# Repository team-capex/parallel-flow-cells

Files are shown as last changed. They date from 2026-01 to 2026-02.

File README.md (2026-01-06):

# User Guide for Parallel MEA / H-Cell Setups

## Install Dependencies from PyProject

Build venv in root directory:

```
python -m venv .venv
```

Upgrade pip:

```
.venv/bin/pip install --upgrade pip
```

Install dependencies into new venv:

```
.venv/bin/pip install -e .
```

Activate venv:

```
source .venv/bin/activate
```

Note: Replace *bin* with *Scripts* if using windows.

## Calibrating Load Cells

## Other Requirements

- Platformio vscode extension to flash firmware to PCBs
- RS485 converter for MFC

## Hardware References

See [BOM](part_files/BOM.pdf) for complete list.

1. [1kg load cells](https://www.digikey.dk/da/products/detail/adafruit-industries-llc/4540/12323569?srsltid=AfmBOop3O_A9xKGq612NTgOTVNnTNE8ITZH4t8R0--68j-zy2UcEIYY0)
2. [0.5slm MFC](https://sensirion.com/products/catalog/SFC5500-05slm)
3. [5slm MFC](https://sensirion.com/products/catalog/SFC6000D-5slm)
4. [3/2 Solenoid Valves](https://www.festo.com/dk/en/a/196132/)
5. [9QX Peristaltic Pump](https://www.boxerpumps.com/peristaltic-pumps-for-liquid/9qx/)

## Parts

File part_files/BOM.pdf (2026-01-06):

Part Number Description Material Cost (DKK) Qty Total DKK Supplier Link MEA x6
| Custom cells | Titanium Grade 2 | | | 4,800.00 kr. WeNext
5004A11 | Toggle clamp | Steel | 118.00 kr. | 6 | 708.00 kr. Goodhand | https://goodhanduk.co.uk/vertical-toggle-clamps/vertical-toggle-clamp-overall-height-60mm-overall-length-94mm-holding-force-150dan-adjustable-flat-101-200kg-51-100mm-51-100mm-21-30mm-51-75mm-m8-gh-13007
| OR 18,77 X 1,78 | Viton/EPDM | 6.30 kr. | 6 | 37.80 kr. MW | https://ehandel.mw.dk/da/178-viton/o-ring-1877x178-viton-
| Barbed to Male 1/4"-28, ID 1/16" | ETFE | 430.00 kr. | 2 | 860.00 kr. Darwin | https://darwin-microfluidics.com/products/barbed-to-male-1-4-28-adapter-for-1-16-or-1-8-id-flexible-tubing-pack-of-10
| Platinum-cured Silicone Tubing (15 m) 2mm ID | Silicone | 178.00 kr. | 1 | 178.00 kr. Darwin
HPS-6-3.1-18-N | Plastic spacer (m3 x 6mm dia) | Nylon | 2.00 kr. | 36 | Accu | https://www.accu.co.uk/cylindrical-spacers/463974-HPS-6-3-1-18-N
SSCF-M4-35-A2 | M4x35mm | A2 | | 24 | Accu
SSCF-M3-25-A2 | M3x25mm | A2 | | 36 | Accu
SSCF-M3-10-A2 | M3x10mm | A2 | | 24 | 600.00 kr. Accu

CO2
1649-SFC6000D-5SLM-ND | MFC for CO2 (I2C, 24V, 210mA) | | 2,174.00 kr. | 1 | 2,174.00 kr. Digikey | https://www.digikey.dk/da/products/detail/sensirion-ag/sfc6000d-5slm/17829202
1528-4545-ND | 6mm PVC tubing | PVC | 12.00 kr. | 1 | 12.00 kr. Digikey | https://www.digikey.dk/da/products/detail/adafruit-industries-llc/4545/11627733?gclsrc=aw.ds&gad_source=1&gad_campaignid=19553954322&gbraid=0AAAAADrbLljpWXnvO9wyNsjCb2PZ5PgfI&gclid=Cj0KCQjw58PGBhCkARIsADbDilx9DRJTLxXdIQNYD9Ui8bdA7DL3JmfsgUJsoTZtAmLSkMoV-oUUZvMaAtvrEALw_wcB
4829-MA08FAHD04RA-20CB25-ND | M8 4p cable | | 57.00 kr. | 1 | 57.00 kr. Digikey | https://www.digikey.dk/da/products/detail/finecables/MA08FAHD04RA-20CB25/18077552?gclsrc=aw.ds&gad_source=1&gad_campaignid=19561463036&gbraid=0AAAAADrbLlhww0wDtSavdPzRh915kKBFp&gclid=Cj0KCQjw58PGBhCkARIsADbDilz7R3Wi_kISS25-sVtoRoq_2h4j312e7uNhwl514B2i2WKu11Ijz_waApS6EALw_wcB
WM17189-ND | Molex Micro-Lock Plus 0451110606 | | 19.00 kr. | 1 | 19.00 kr. Digikey | https://www.digikey.dk/da/products/detail/molex/0451110606/7915903?s=N4IgTCBcDaILIHsA2BTAHgAjgSwMYCcEBaAGQVwGsMAFJAVwGcMAGAFgFYBGb5gNj5ABdAL5A
FR-4-1/4 | Distributor Block, 3 Outlet, G1/4, FR Series | Al | 140.00 kr. | 3 | 420.00 kr. RS | https://dk.rs-online.com/web/p/manifold-baser-undersegmenter-og-endesegmenter/2890837?cm_mmc=DK-PLA-DS3A-_-google-_-CSS_DK_DK_PMax_Low-Price-Low-Performance-_--_-2890837&matchtype=&&gclsrc=aw.ds&gad_source=1&gad_campaignid=22922140264&gbraid=0AAAAADkeWNPjzJvbKHpMcgwmJvPYL_CWR&gclid=Cj0KCQjwrc7GBhCfARIsAHGcW5Vg9IRaZ06QjpGmncXCGT5fjW5V8vwqqtyP1wgSseHVZzooB2Mm_mAaAqvkEALw_wcB
QS-G1/4-6 | Pneumatic Fitting, Push-In Fitting, G1/4, 14 bar, 6 mm, Brass, QS (10) | Brass | 196.00 kr. | 1 | 196.00 kr. RS | https://dk.farnell.com/festo/qs-g1-4-6/push-in-fitting-6mm-g1-4/dp/3432186
B-1/4 | Pneumatic Fitting, Push-In Fitting, G1/4, 18 mm, Steel, (10) | Steel | 114.00 kr. | 1 | 114.00 kr. RS | https://dk.farnell.com/festo/b-1-4/push-in-fitting-18mm-g1-4/dp/3436726
QSF-1/4-4-B | Pneumatic Fitting, Push-In Fitting, G1/4, 14 bar, 4 mm, Brass, QSF | Brass | 33.00 kr. | 6 | 198.00 kr. Farnell | https://dk.farnell.com/festo/qsf-1-4-4-b/push-in-fitting-4mm-g1-4-9-7mm/dp/3432275?gross_price=true&CMP=KNC-GDK-GEN-Shopping-Pmax-High-ROAS-Test-1333&mckv=_dc|pcrid||&gad_source=1&gad_campaignid=20746710150&gbraid=0AAAAAD8yeHkMi_H50LZUAWp5PPbQ_94pU&gclid=CjwKCAjw89jGBhB0EiwA2o1Onx2IczdmaHkpGrZ8EoYNKaaRZJsceP5hbWil1OpdHAXtCcThY-iGPhoCY5EQAvD_BwE
NPFC-D-2G14-M | Festo NPFC Lige fitting G 1/4, G 1/4 han til G 1/4, Med gevind | Brass | 68.00 kr. | 1 | 68.00 kr. RS | https://dk.rs-online.com/web/p/pneumatik-fittings/2502692?cm_mmc=DK-PLA-DS3A-_-google-_-CSS_DK_DK_PMax_Low-Price-Low-Performance-_--_-2502692&matchtype=&&gclsrc=aw.ds&gad_source=1&gad_campaignid=22922140264&gbraid=0AAAAADkeWNMbt_YSda_Ss2Pe8KWR1JZ7d&gclid=CjwKCAjw89jGBhB0EiwA2o1On4_b-wo6nXAr70IkGOkNC9hPqeI6ZpGywWgbqwnNWUBGY88c-LlPtBoCWeoQAvD_BwE
QSM-M3-4-I | Pneumatic Fitting, Push-In Fitting, M3, 14 bar, 4 mm, Steel, QSM | Steel | 30.00 kr. | 12 | 360.00 kr. Farnell | https://dk.farnell.com/festo/153314/push-in-fitting-4mm-m3-8mm/dp/3432137?gross_price=true&CMP=KNC-GDK-GEN-Shopping-Pmax-High-ROAS-Test-1333&mckv=_dc|pcrid||&gad_source=1&gad_campaignid=20746710150&gbraid=0AAAAAD8yeHkMi_H50LZUAWp5PPbQ_94pU&gclid=CjwKCAjw89jGBhB0EiwA2o1On-xq_k4-8pehjHkxhBXVDBrv5aZdelxS_hp0dAAXmB-WaFDIt3CJrRoCQbAQAvD_BwE
QSMT-4 | Pneumatic Fitting, Push-In T-Fitting, 14 bar, 4 mm, PBT (Polybutylene Terephthalate), QST | PBT | 33.00 kr. | 5 | 165.00 kr. Farnell | https://dk.farnell.com/festo/153128/push-in-t-fitting-4mm-10mm/dp/3432081?gross_price=true&CMP=KNC-GDK-GEN-Shopping-Pmax-High-ROAS-Test-1333&mckv=_dc|pcrid||&gad_source=1&gad_campaignid=20746710150&gbraid=0AAAAAD8yeHkMi_H50LZUAWp5PPbQ_94pU&gclid=CjwKCAjw89jGBhB0EiwA2o1On9Ke7jQRASimdTHQLkaKA-uQwV2e4eMabnsTtx5DLgJlGQeRKKp_ehoCmqwQAvD_BwE
PEN-4X0,75-BL | Pneumatic Tubing, 4 mm, 2.7 mm, PE (Polyethylene), Blue, 10 bar, 50 m | PE | 164.00 kr. | 1 | 164.00 kr. Farnell | https://dk.farnell.com/festo/pen-4x0-75-bl/plastic-tubing-10bar-pe-50m-blue/dp/3432523?gross_price=true&CMP=KNC-GDK-GEN-Shopping-Pmax-High-ROAS-Test-1333&mckv=_dc|pcrid||&gad_source=1&gad_campaignid=20746710150&gbraid=0AAAAAD8yeHkMi_H50LZUAWp5PPbQ_94pU&gclid=CjwKCAjw89jGBhB0EiwA2o1OnzBm_ssv7OcDU8E3JuuKJTVj9dxXW-fRRRptIhBTt02IWX2fsSySehoCNBcQAvD_BwE
304-005 | RS PRO 24V dc AC/DC-adapter, Ekstern strømforsyning, 1A, 24W, Europæisk stik | | 134.00 kr. | 1 | 134.00 kr. RS | https://dk.rs-online.com/web/p/ac-dc-adaptere/0304005?srsltid=AfmBOoqRQSO9QZzJjiM4ApOePkaanLnN2yxJvQekZTMz0jzVhUAgkOK8KCM
MHE2-M1H-3/2O-M7 | Air Solenoid Valve, 3/2 Way, Closed, QS-4, -0.9 bar to 8 bar, 100 l/min | | 300.00 kr. | 6 | 1,800.00 kr. Rowse | https://www.rowse-pneumatics.co.uk/festo-mhe2-m1h-3-2g-qs-4
QSM-M7-4-I | Male thread M7 to 4mm tubing | | 222.00 kr. | 1 | 222.00 kr. WATTOO | https://www.wattoo.dk/festo-lige-forskruning-indstik-qsm-m7-4-i-10-stk-3980020634#ws-productView-desc
1649-SFC5500-0.5SLM-ND | MFC for CO2 (I2C, 24V, 210mA) | | 9,600.00 kr. | 1 | Digikey | https://www.digikey.dk/da/products/detail/sensirion-ag/sfc6000d-5slm/17829202
QSM-M3-4-I | Pneumatic Fitting, Push-In Fitting, M3, 14 bar, 4 mm, Steel, QSM | Steel | 30.00 kr. | 4 | 120.00 kr. Farnell | https://dk.farnell.com/festo/153314/push-in-fitting-4mm-m3-8mm/dp/3432137?gross_price=true&CMP=KNC-GDK-GEN-Shopping-Pmax-High-ROAS-Test-1333&mckv=_dc|pcrid||&gad_source=1&gad_campaignid=20746710150&gbraid=0AAAAAD8yeHkMi_H50LZUAWp5PPbQ_94pU&gclid=CjwKCAjw89jGBhB0EiwA2o1On-xq_k4-8pehjHkxhBXVDBrv5aZdelxS_hp0dAAXmB-WaFDIt3CJrRoCQbAQAvD_BwE
QSM-M5-4-I | Pneumatic Fitting, Push-In Fitting, M5, 14 bar, 4 mm, Steel, QSM | Steel | 30.00 kr. | 4 | 120.00 kr. RS | https://dk.rs-online.com/web/p/pneumatik-fittings/1216038

Liquids
| 9800.73 9QX stepper 3 roller (ID Ø 3.5 mm - single) | | 962.00 kr. | 2 | 1,924.00 kr. Boxer
| 9000.324 9QX 3.5mm ID tubing | Innovasil | 90.00 kr. | 2 | 180.00 kr. Boxer
| T-fittings for liquid manifold: 3.2mm ID (5 per manifold) | PP | 380.00 kr. | 1 | 380.00 kr. Darwin | https://darwin-microfluidics.com/products/masterflex-t-barb-connectors-pack-of-10
| Platinum-cured Silicone Tubing (15 m) 2 or 3mm ID | Silicone | 178.00 kr. | 1 | 178.00 kr. Darwin
102-PH-008-4MM | 100 Series Micro Peristaltic Pump (0.8mm Viton tubing) | | 140.00 kr. | 4 | 560.00 kr. Williamson | https://www.wmcpumps.com/SKU1-134
8HS15-0304S | Nema 11 Bipolar 1.8deg 4Ncm(5.7oz.in) 0.6A 20x20x39.3mm 4 Wires | | 120.00 kr. | 4 | 480.00 kr. StepperOnline | https://www.omc-stepperonline.com/nema-8-bipolar-1-8deg-3ncm-4-25oz-in-0-3a-12v-20x20x38mm-4-wires-8hs15-0304s
| Mini Peristaltic Pump | | 100.00 kr. | 8 | 800.00 kr. Frugo | https://www.fruugo.dk/mini-peristaltic-pump-high-quality-for-laboratory-bioengineering-g528-dc12vtype-c/p-314459620-701052377?language=en&ac=google&utm_source=google&utm_medium=paid&asc=pmax&gad_source=1&gad_campaignid=20975253578&gbraid=0AAAAADpXug2rU-1W62fdGEQqKVeoOzLIN&gclid=Cj0KCQiAgvPKBhCxARIsAOlK_Erhti6nMGFpah9tsT6SidzKpgmbqzjA4kZy3KL463TXhfh0PgX31E4aAvdfEALw_wcB
EGS11-G10 | EG Series Planetary Gearbox Gear Ratio 10:1 | | 200.00 kr. | 4 | 800.00 kr. StepperOnline | https://www.omc-stepperonline.com/eg-series-planetary-gearbox-gear-ratio-10-1-backlash-15-arc-min-for-nema-11-stepper-motor-egs11-g10
ID-P-642 | Female Luer to Male 10-32 Coned Adapters (pack of 5) | PP | 253.00 kr. | 1 | 253.00 kr. Darwin | https://darwin-microfluidics.com/products/female-luer-to-male-10-32-coned-adapters-pack-of-5
| Male Luer Lock to Barb Adapters | PP | 160.00 kr. | 1 | 160.00 kr. Darwin

HCELL x2
| Custom cells | PEEK/SS | | | 7,750.00 kr. WeNext
| Membrane O-Ring (18x1.5) | Viton | | 1 | 300.00 kr. MWilhelmsen | https://ehandel.mw.dk/da/150---152-viton/o-ring-18x15-viton-

Reference Electrode O-Ring (1.42x1.52) | Viton | 1 | MWilhelmsen | https://ehandel.mw.dk/da/150---152-viton/o-ring-142x152-viton-
PEEK Needle O-Rings (1.42x1.52) | Viton | 1 | MWilhelmsen
Lid O-Ring (12.42x1.78) | Viton | 1 | MWilhelmsen | https://ehandel.mw.dk/da/178-viton/o-ring-1242x178-viton-
Button O-Ring (6.75x1.78) | Viton | 1 | MWilhelmsen | https://ehandel.mw.dk/da/178-viton/o-ring-675x178-viton-
Face Seal O-Ring (15.62x1.78) | Viton | 2 | MWilhelmsen | https://ehandel.mw.dk/da/178-viton/o-ring-156x178-viton-
Sample Holder O-Ring (1.5x13) | FKM | 1 | RS | https://dk.rs-online.com/web/p/pakninger-og-o-ringe/1965679
4mm check valve | | 2 | RS | https://dk.rs-online.com/web/p/pneumatik-kontraventiler/9160934?cm_mmc=DK-PLA-DS3A-_-google-_-CSS_DK_DK_PMax_Low-Price-High-Performance-_--_-9160934&matchtype=&&gclsrc=aw.ds&gad_source=1&gad_campaignid=21368103075&gbraid=0AAAAADkeWNOhqKHZ-wnmj1lLo4dak1vKV&gclid=Cj0KCQjw9obIBhCAARIsAGHm1mTXmxO7bYi1EcSHGXpSH-vTNFiibPHKBHfGIG0wtLczniOT5oRMeXMaArEPEALw_wcB

Other
1528-4540-ND | 1kg Load Cell
| | 4 | 350.00 kr. Digikey | https://www.digikey.dk/da/products/detail/adafruit-industries-llc/4540/12323569?srsltid=AfmBOorwMf2knGiM3Ey5qxezQkc4qGCeHyW89jkVCpoIuLHWATXuRHIX

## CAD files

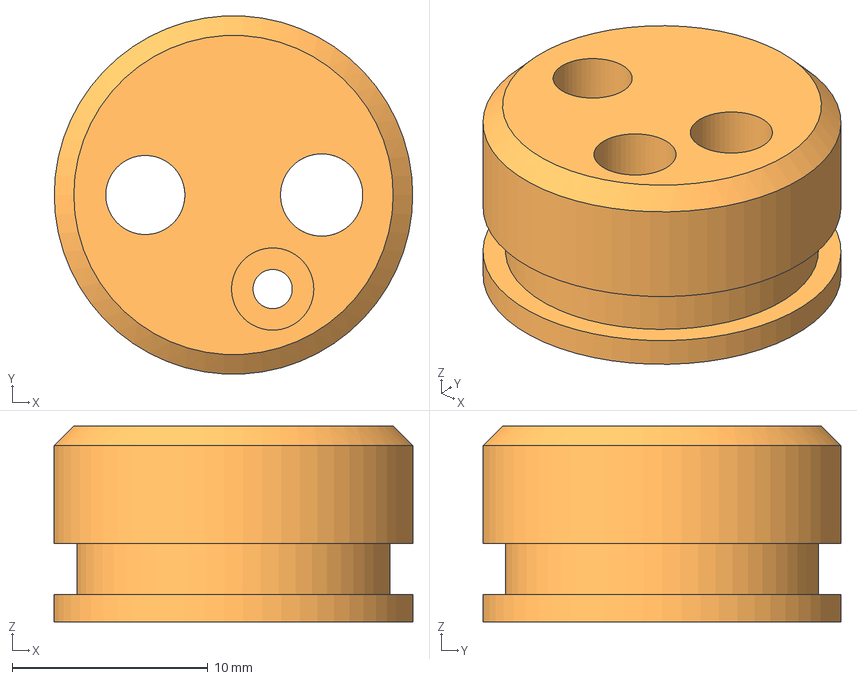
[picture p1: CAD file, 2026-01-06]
part_files/H-Cell - Counter Lid.step
18.3 x 18.3 x 10.0 mm

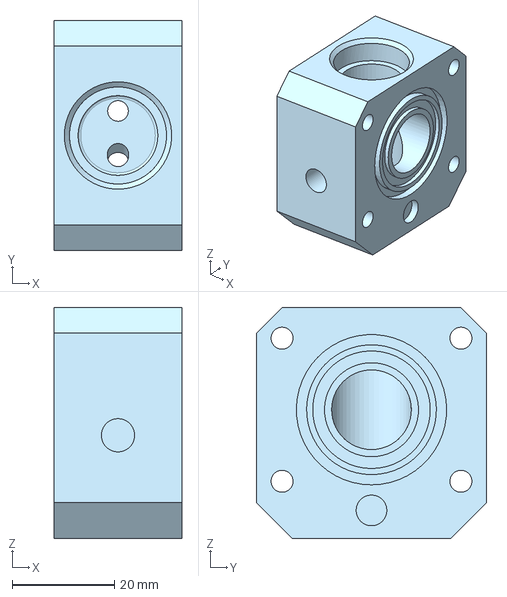
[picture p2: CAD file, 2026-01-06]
part_files/H-Cell - Counter Cell.step
25.0 x 45.0 x 45.2 mm

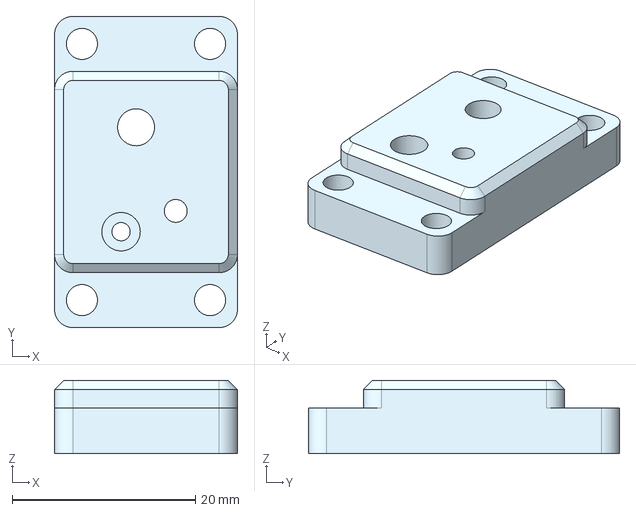
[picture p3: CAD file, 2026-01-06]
part_files/H-Cell - Working Lid.step
20.0 x 34.0 x 8.00 mm

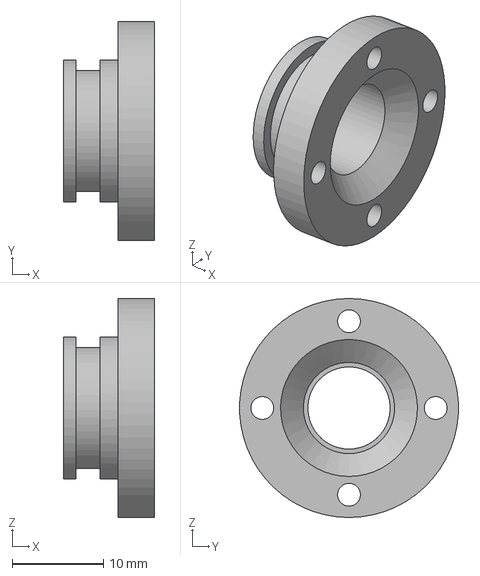
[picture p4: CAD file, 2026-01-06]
part_files/H-Cell - Sample Holder.step
10.0 x 24.0 x 24.0 mm

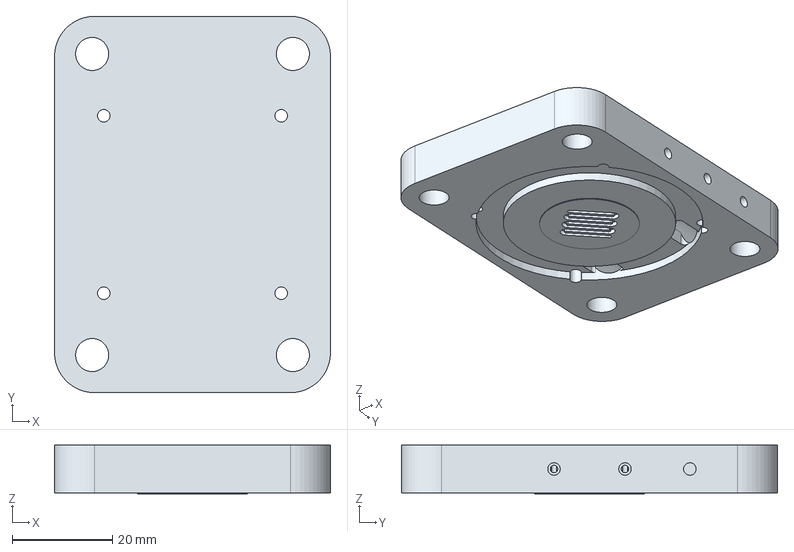
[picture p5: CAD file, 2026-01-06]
part_files/CATHODE_PLATE_TI - REV1.step
55.0 x 75.0 x 9.73 mm

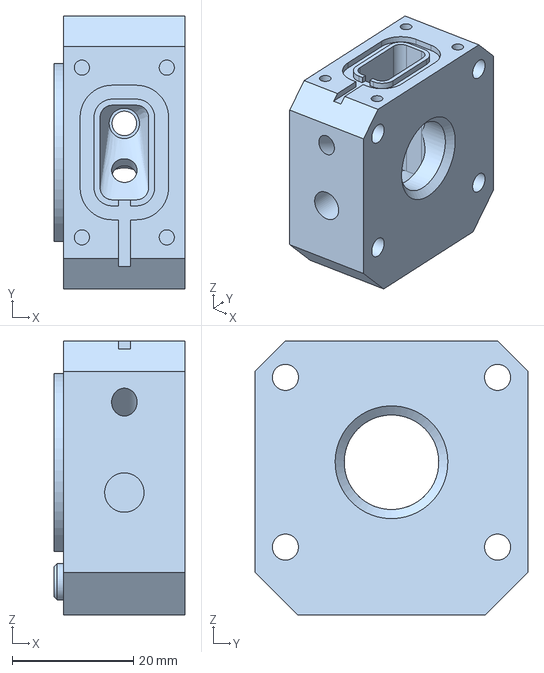
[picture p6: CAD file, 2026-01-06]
part_files/H-Cell - Working Cell.step
21.6 x 45.0 x 45.2 mm

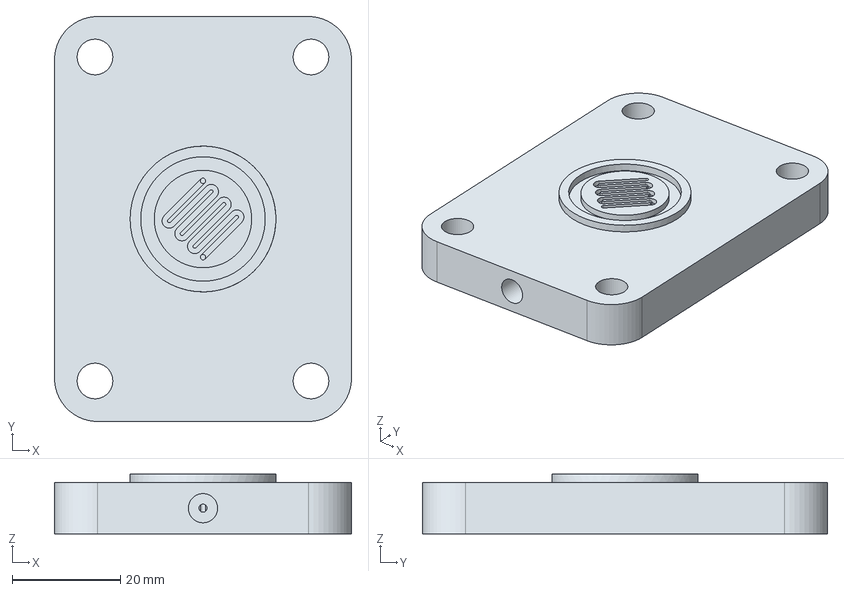
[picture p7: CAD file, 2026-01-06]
part_files/ANODE_PLATE_TI - REV1.step
55.0 x 75.0 x 11.1 mm

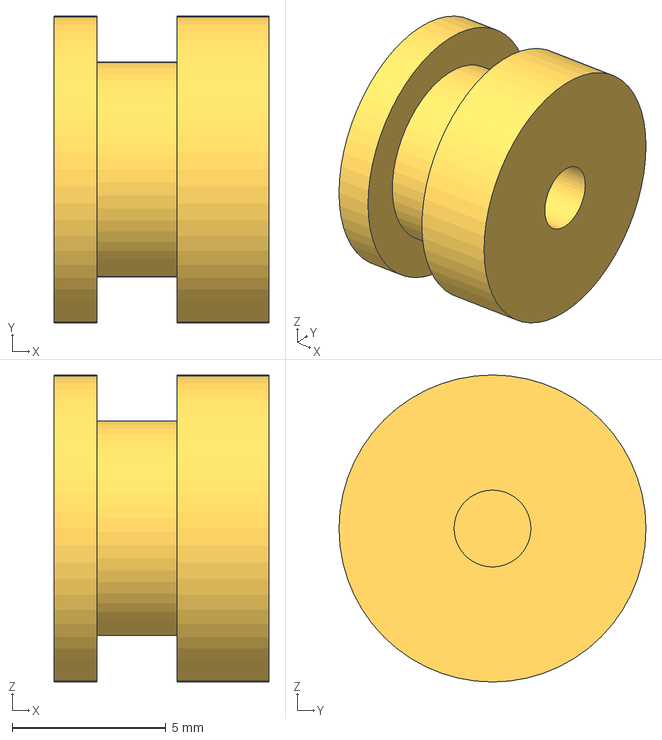
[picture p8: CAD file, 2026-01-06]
part_files/H-Cell - Sample Press.step
7.00 x 10.0 x 10.0 mm

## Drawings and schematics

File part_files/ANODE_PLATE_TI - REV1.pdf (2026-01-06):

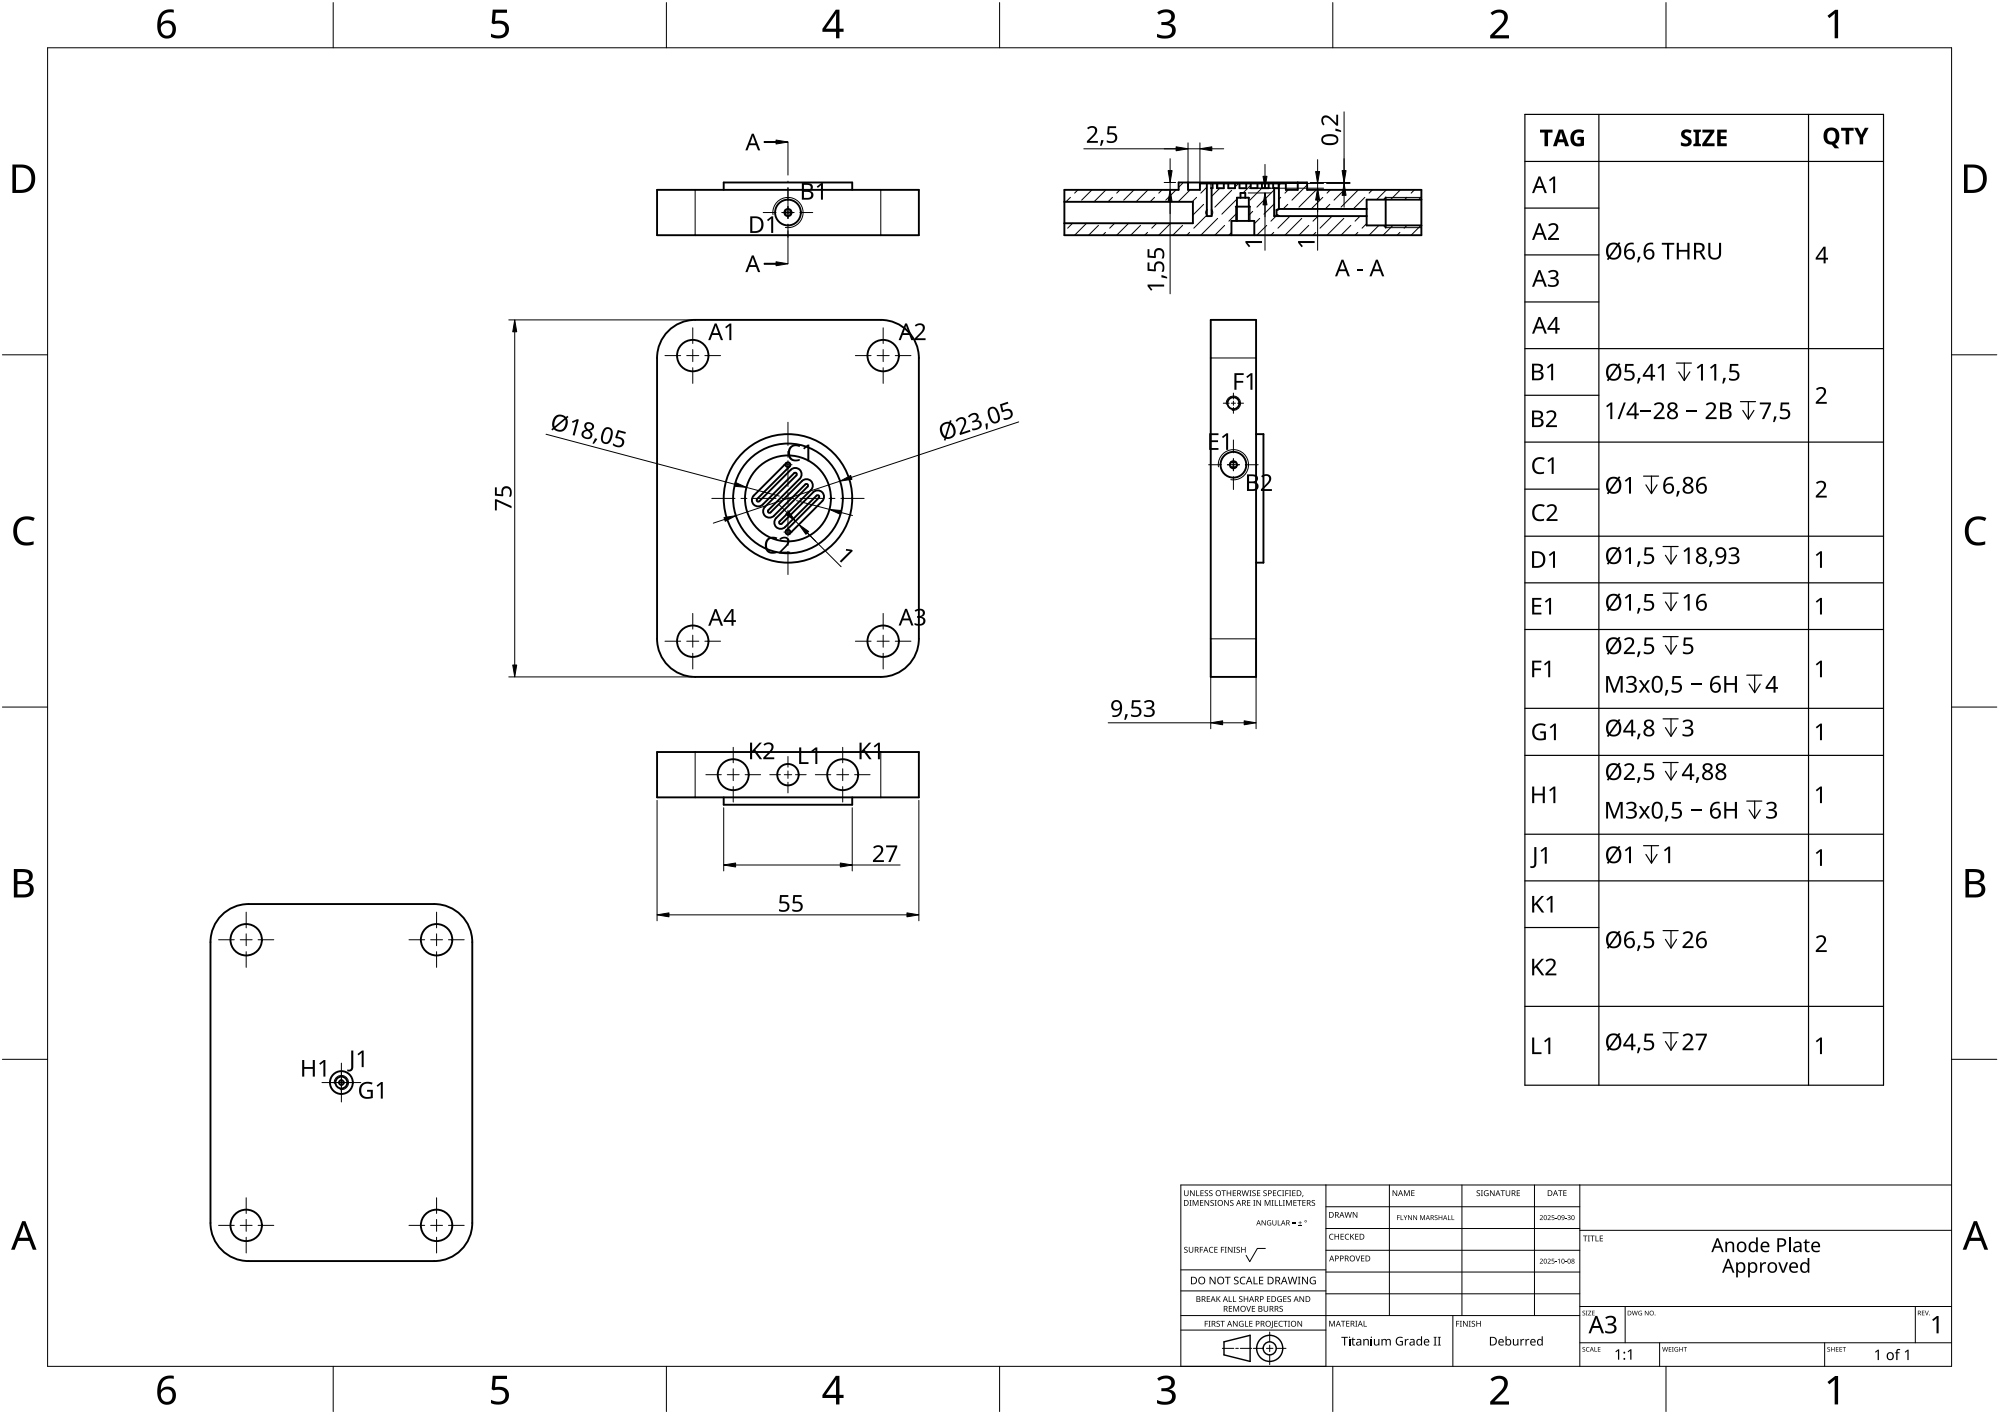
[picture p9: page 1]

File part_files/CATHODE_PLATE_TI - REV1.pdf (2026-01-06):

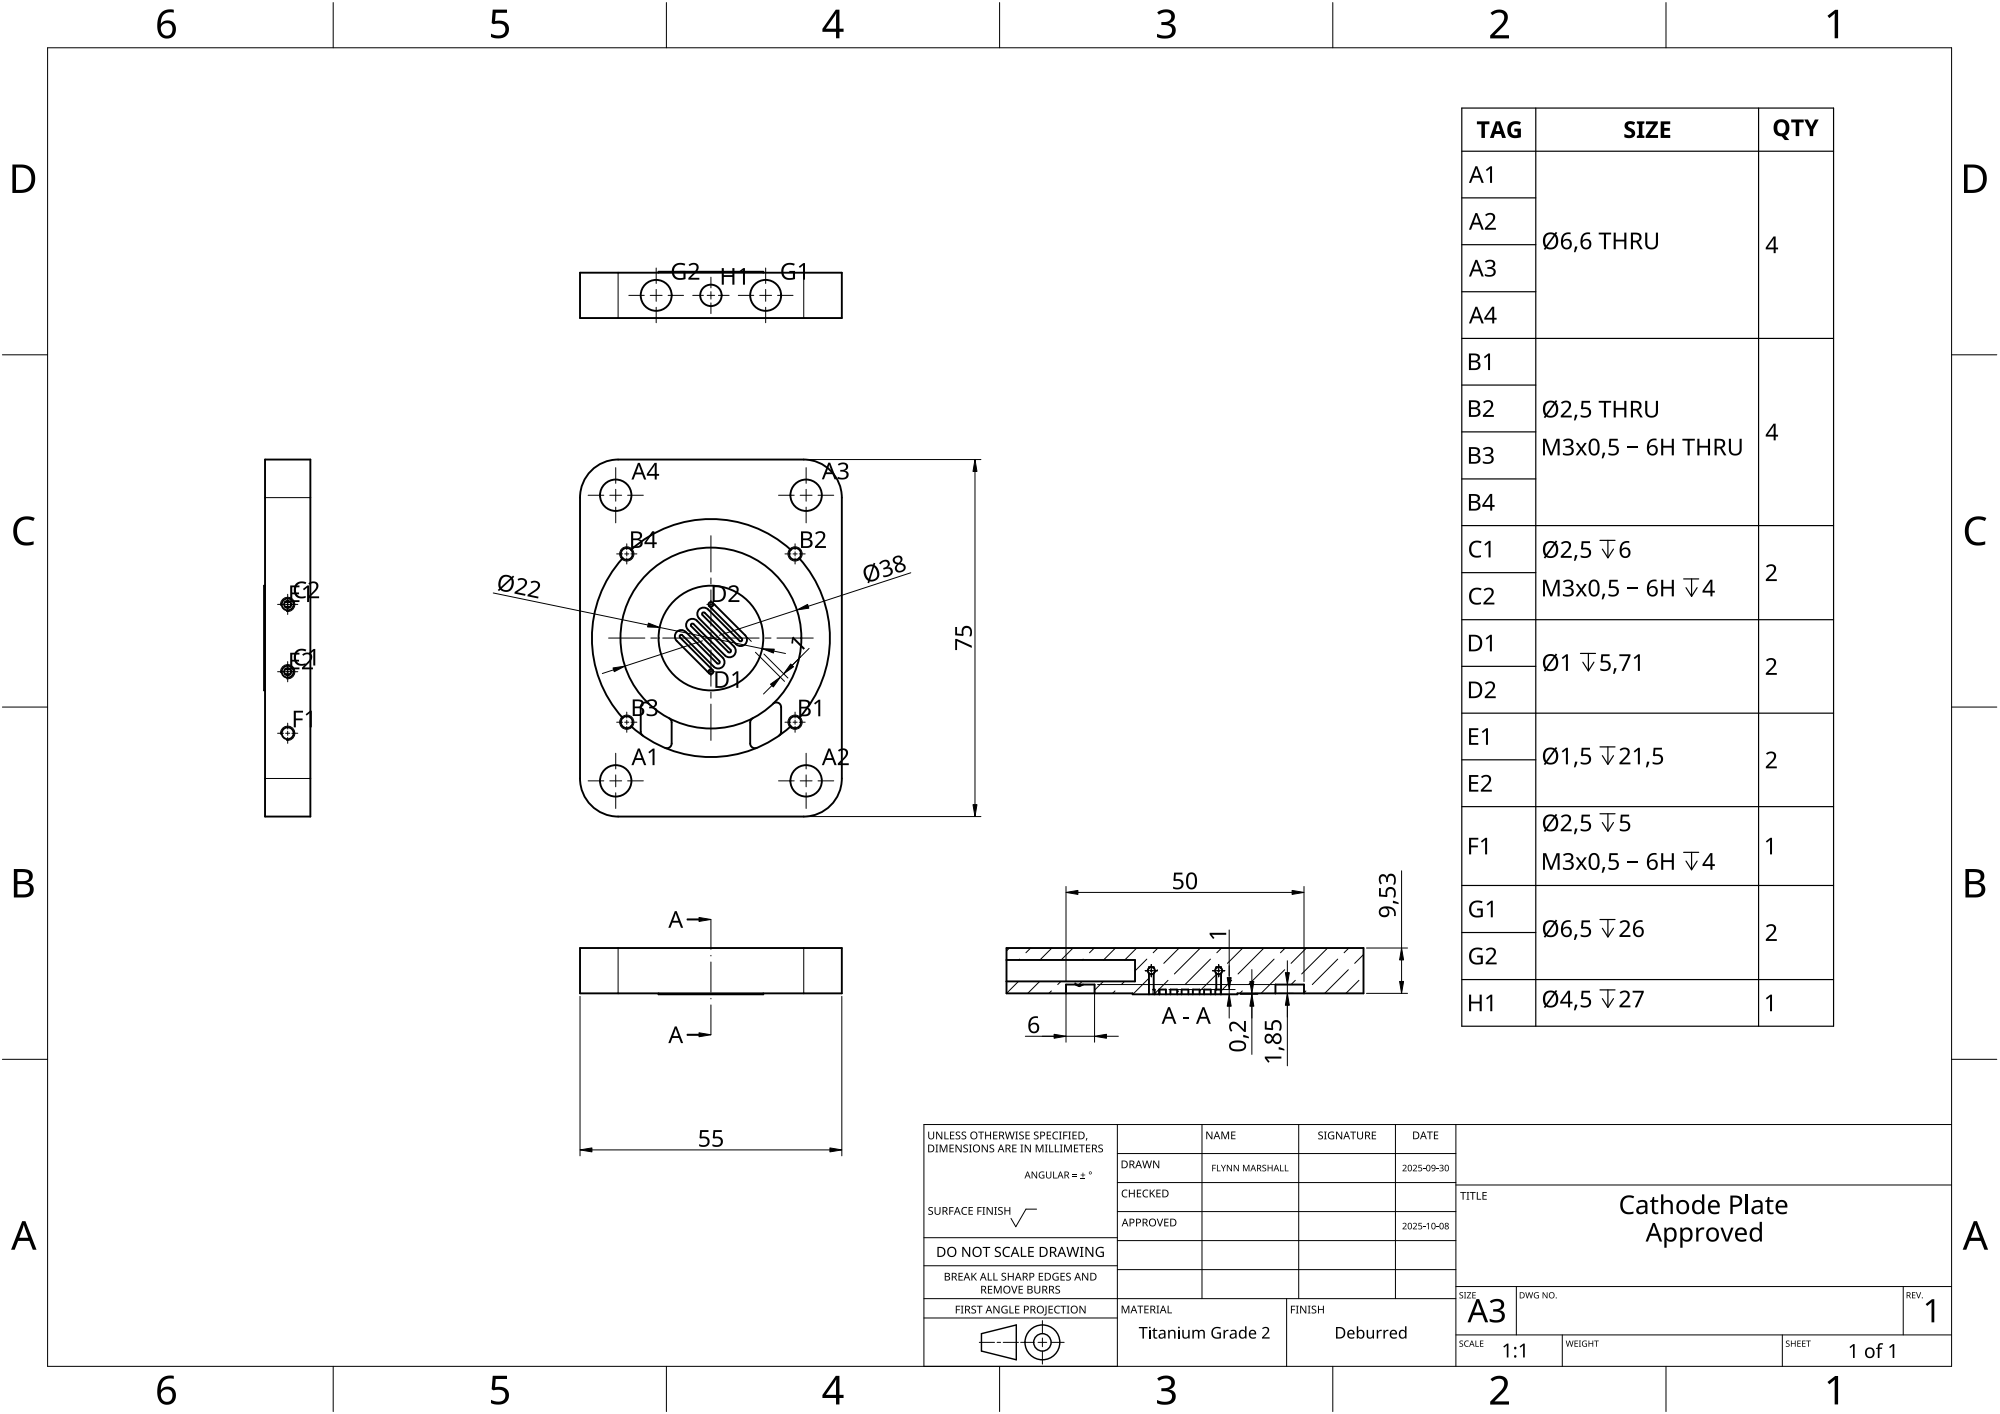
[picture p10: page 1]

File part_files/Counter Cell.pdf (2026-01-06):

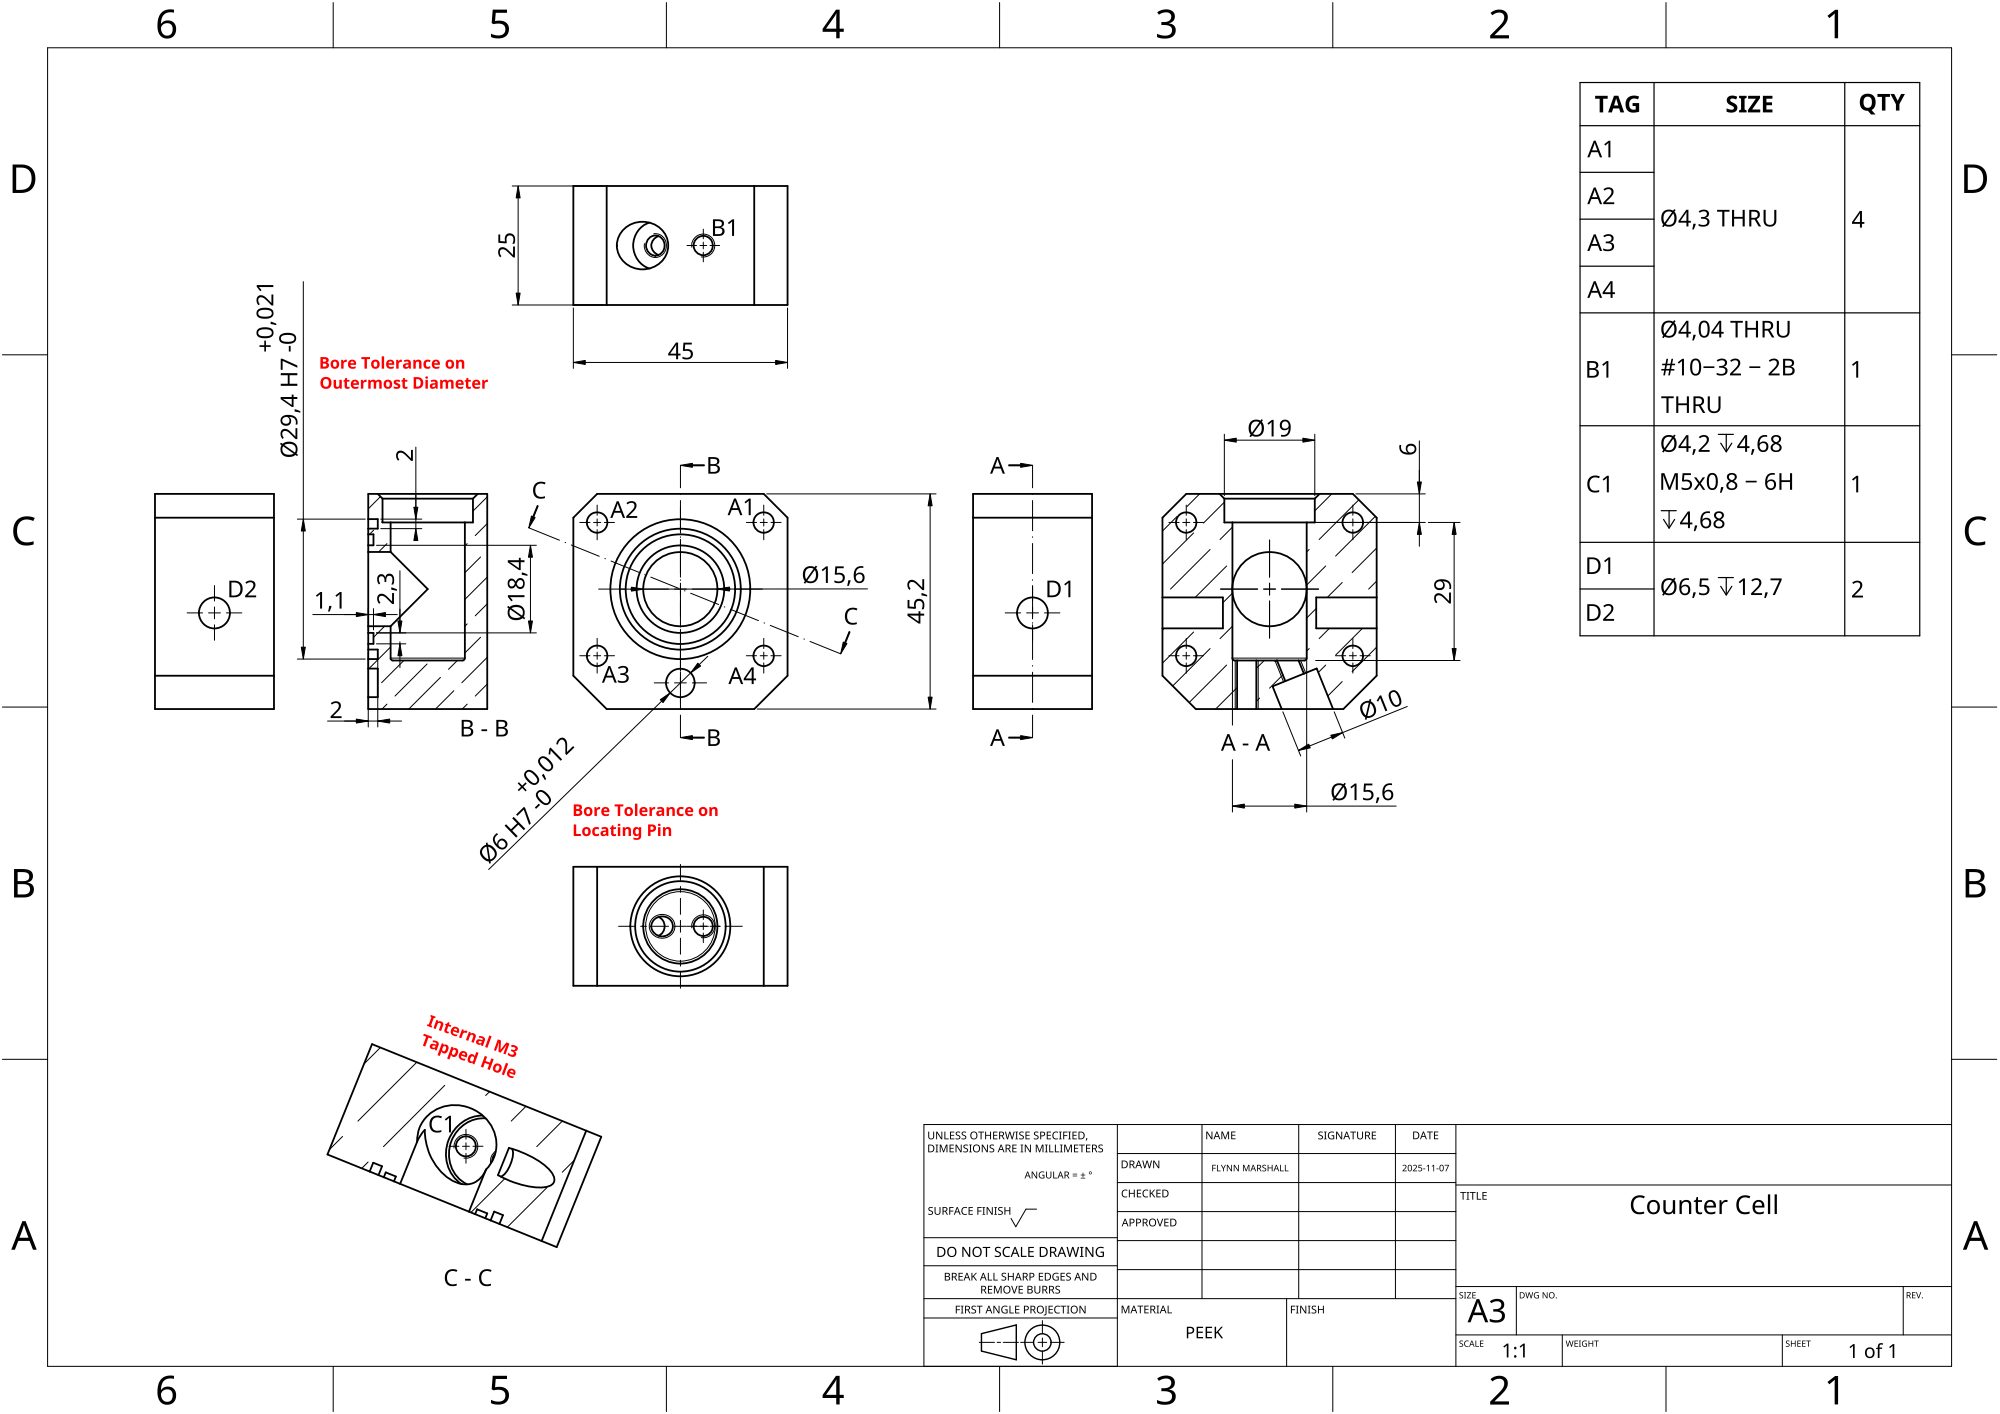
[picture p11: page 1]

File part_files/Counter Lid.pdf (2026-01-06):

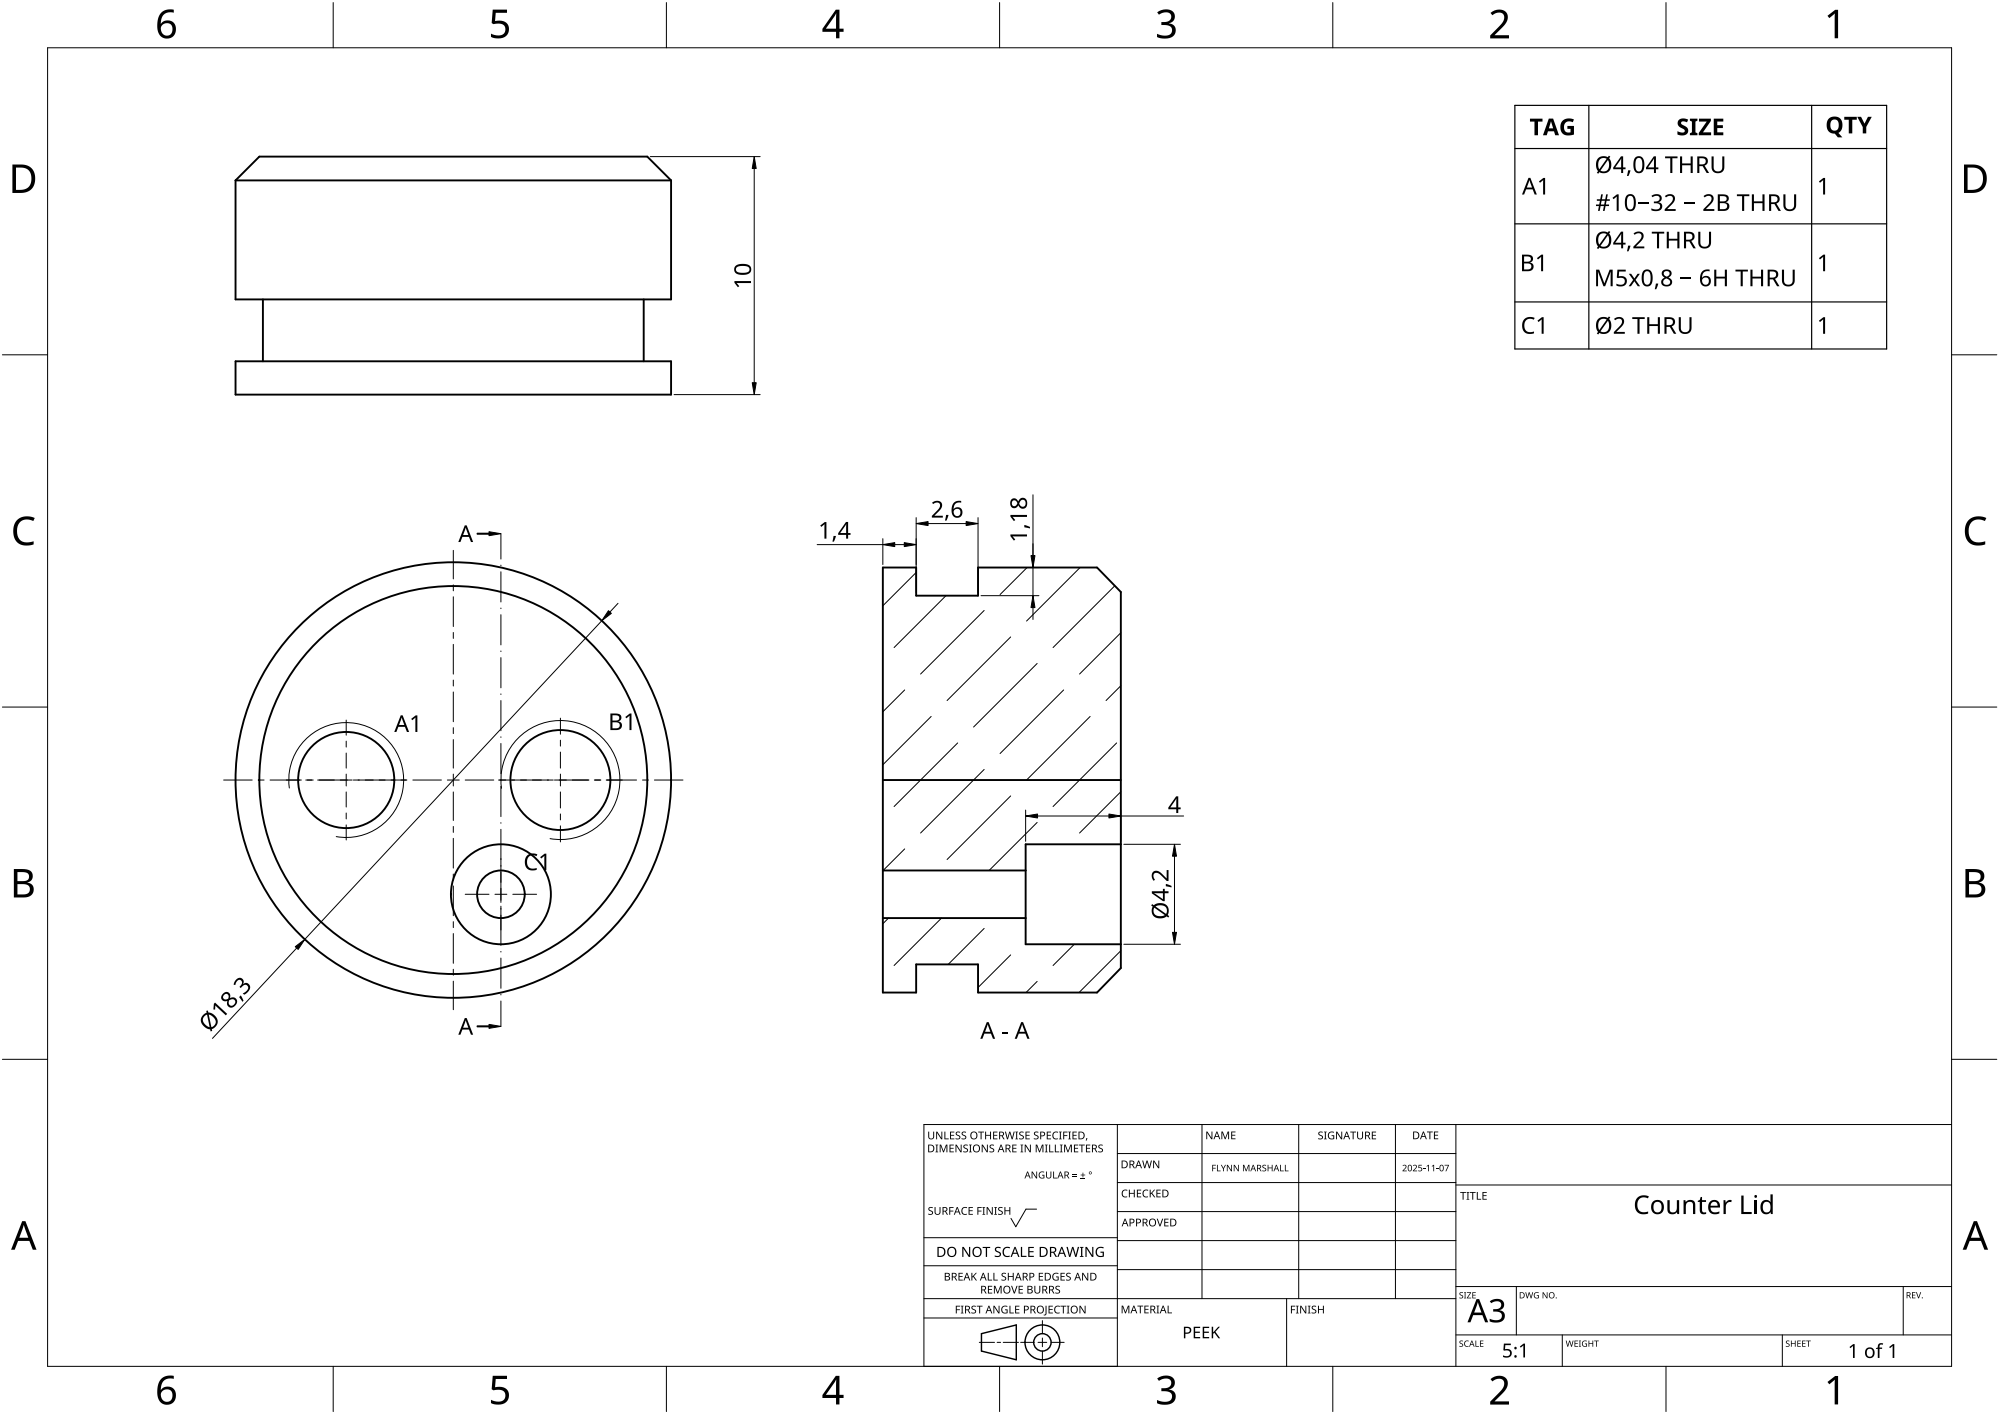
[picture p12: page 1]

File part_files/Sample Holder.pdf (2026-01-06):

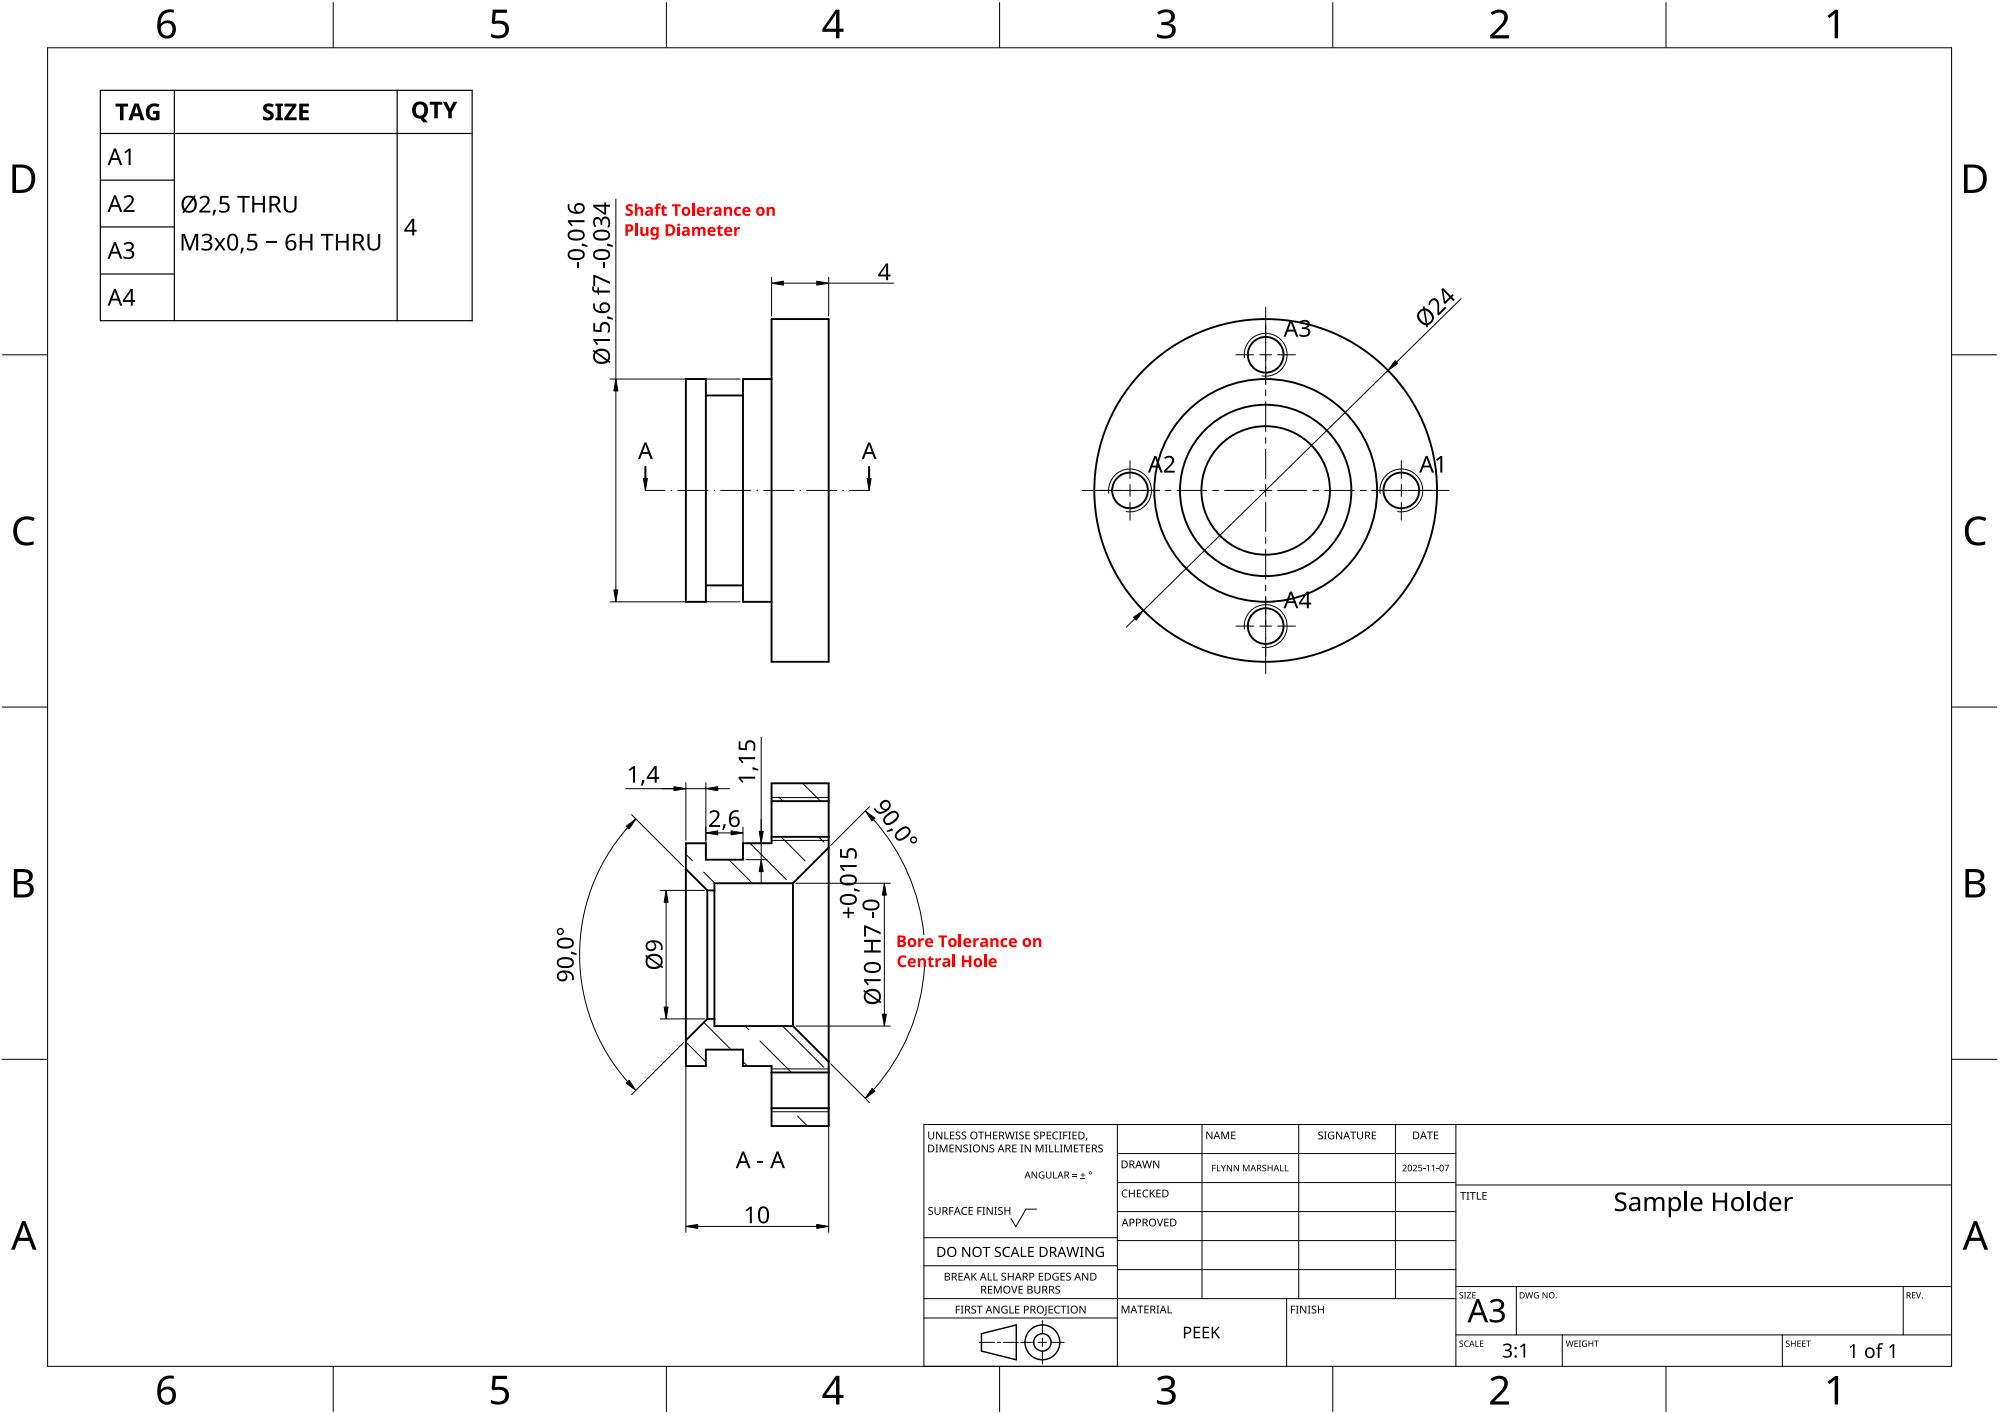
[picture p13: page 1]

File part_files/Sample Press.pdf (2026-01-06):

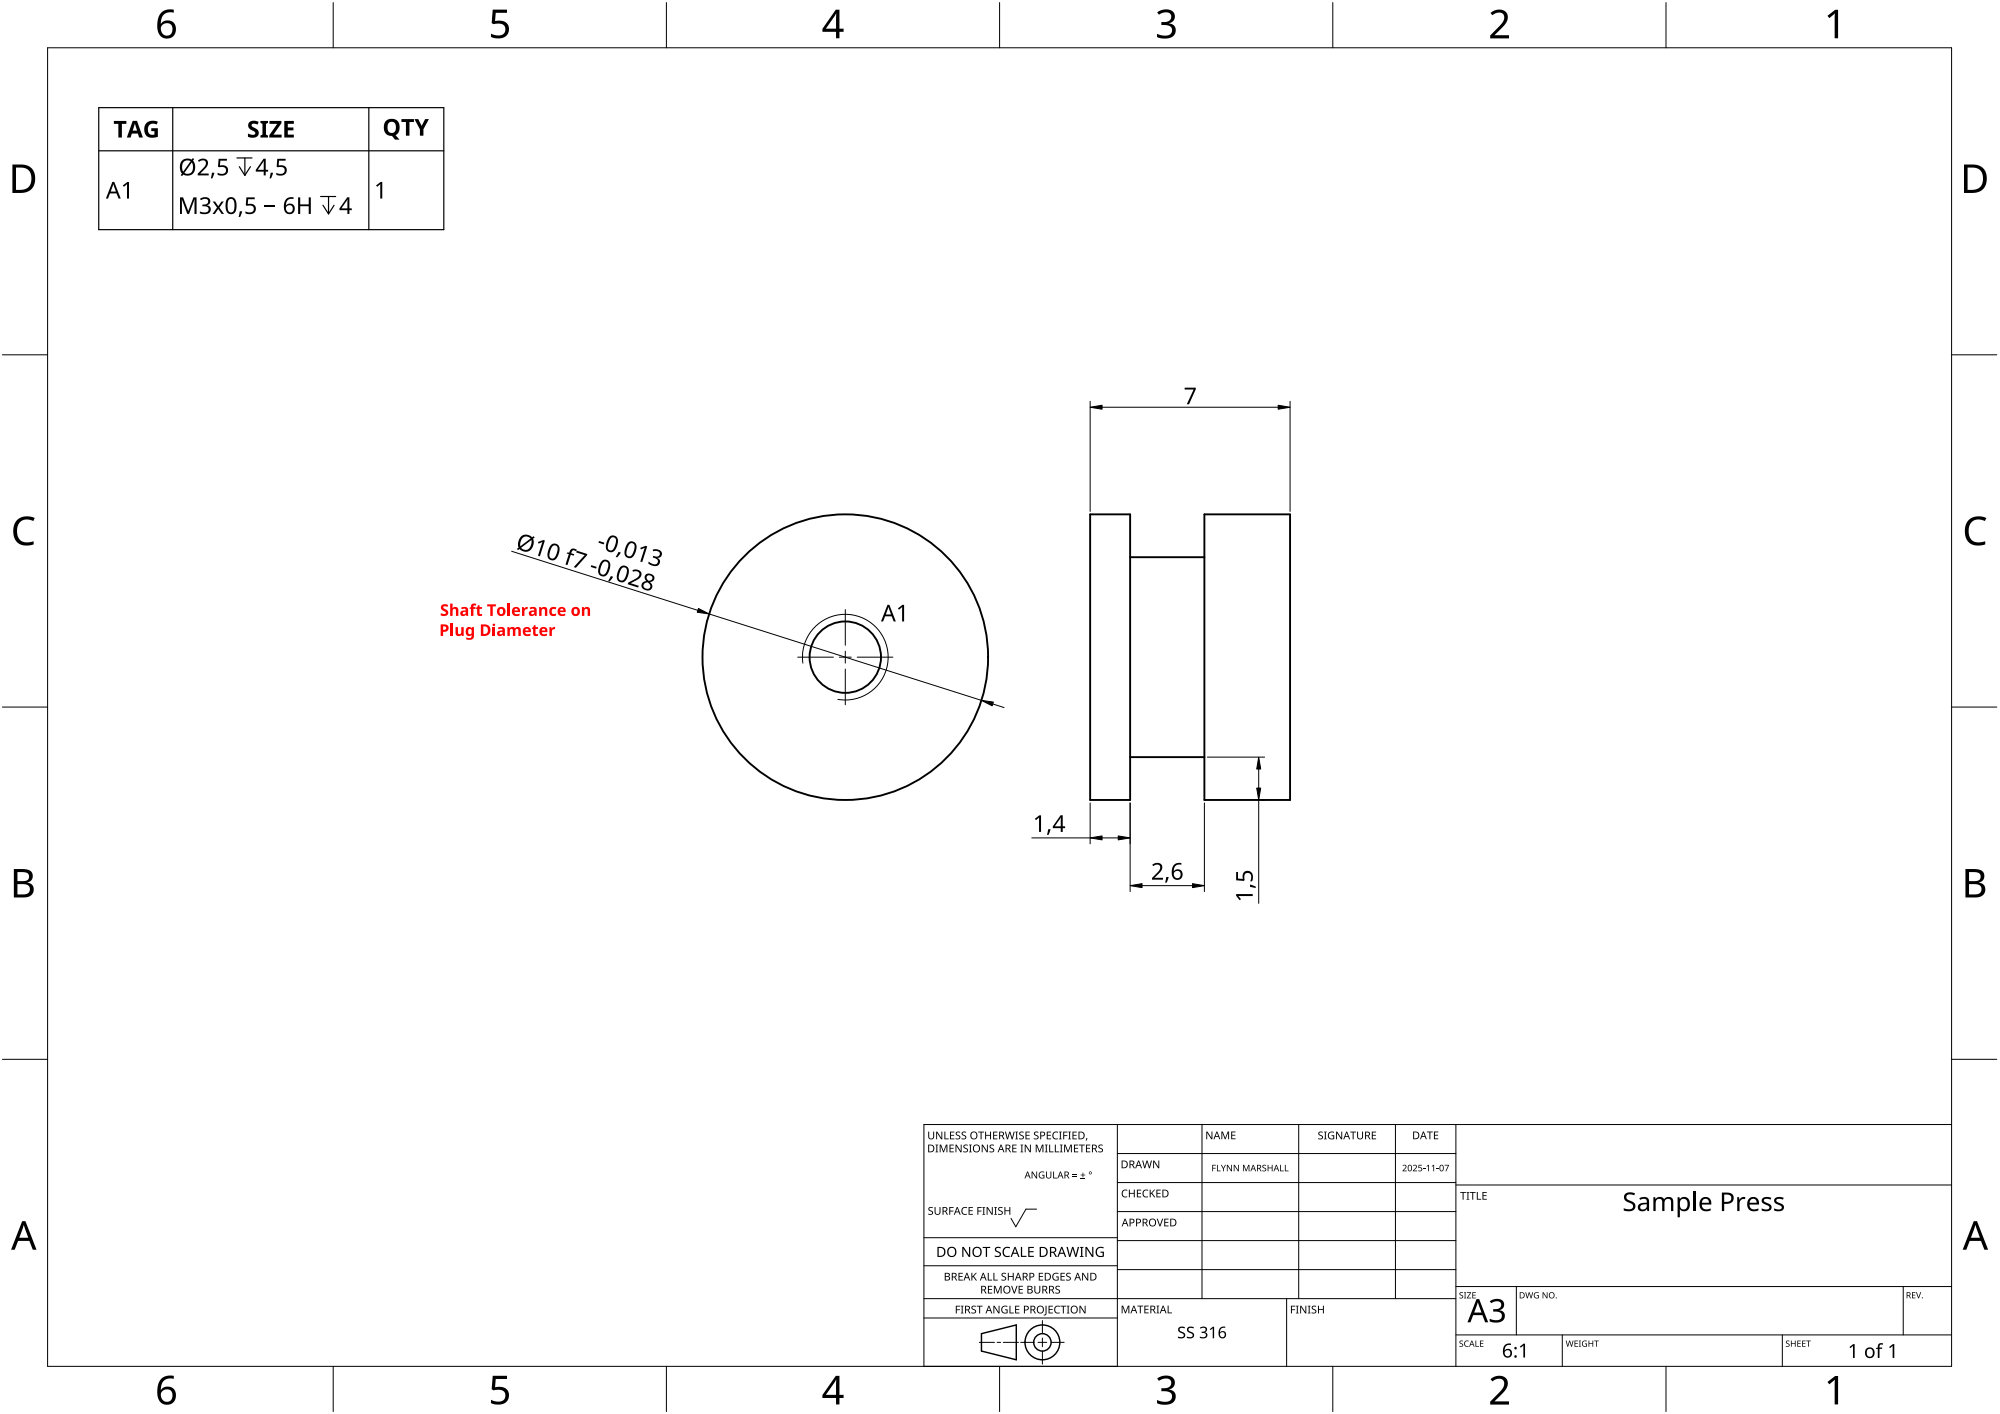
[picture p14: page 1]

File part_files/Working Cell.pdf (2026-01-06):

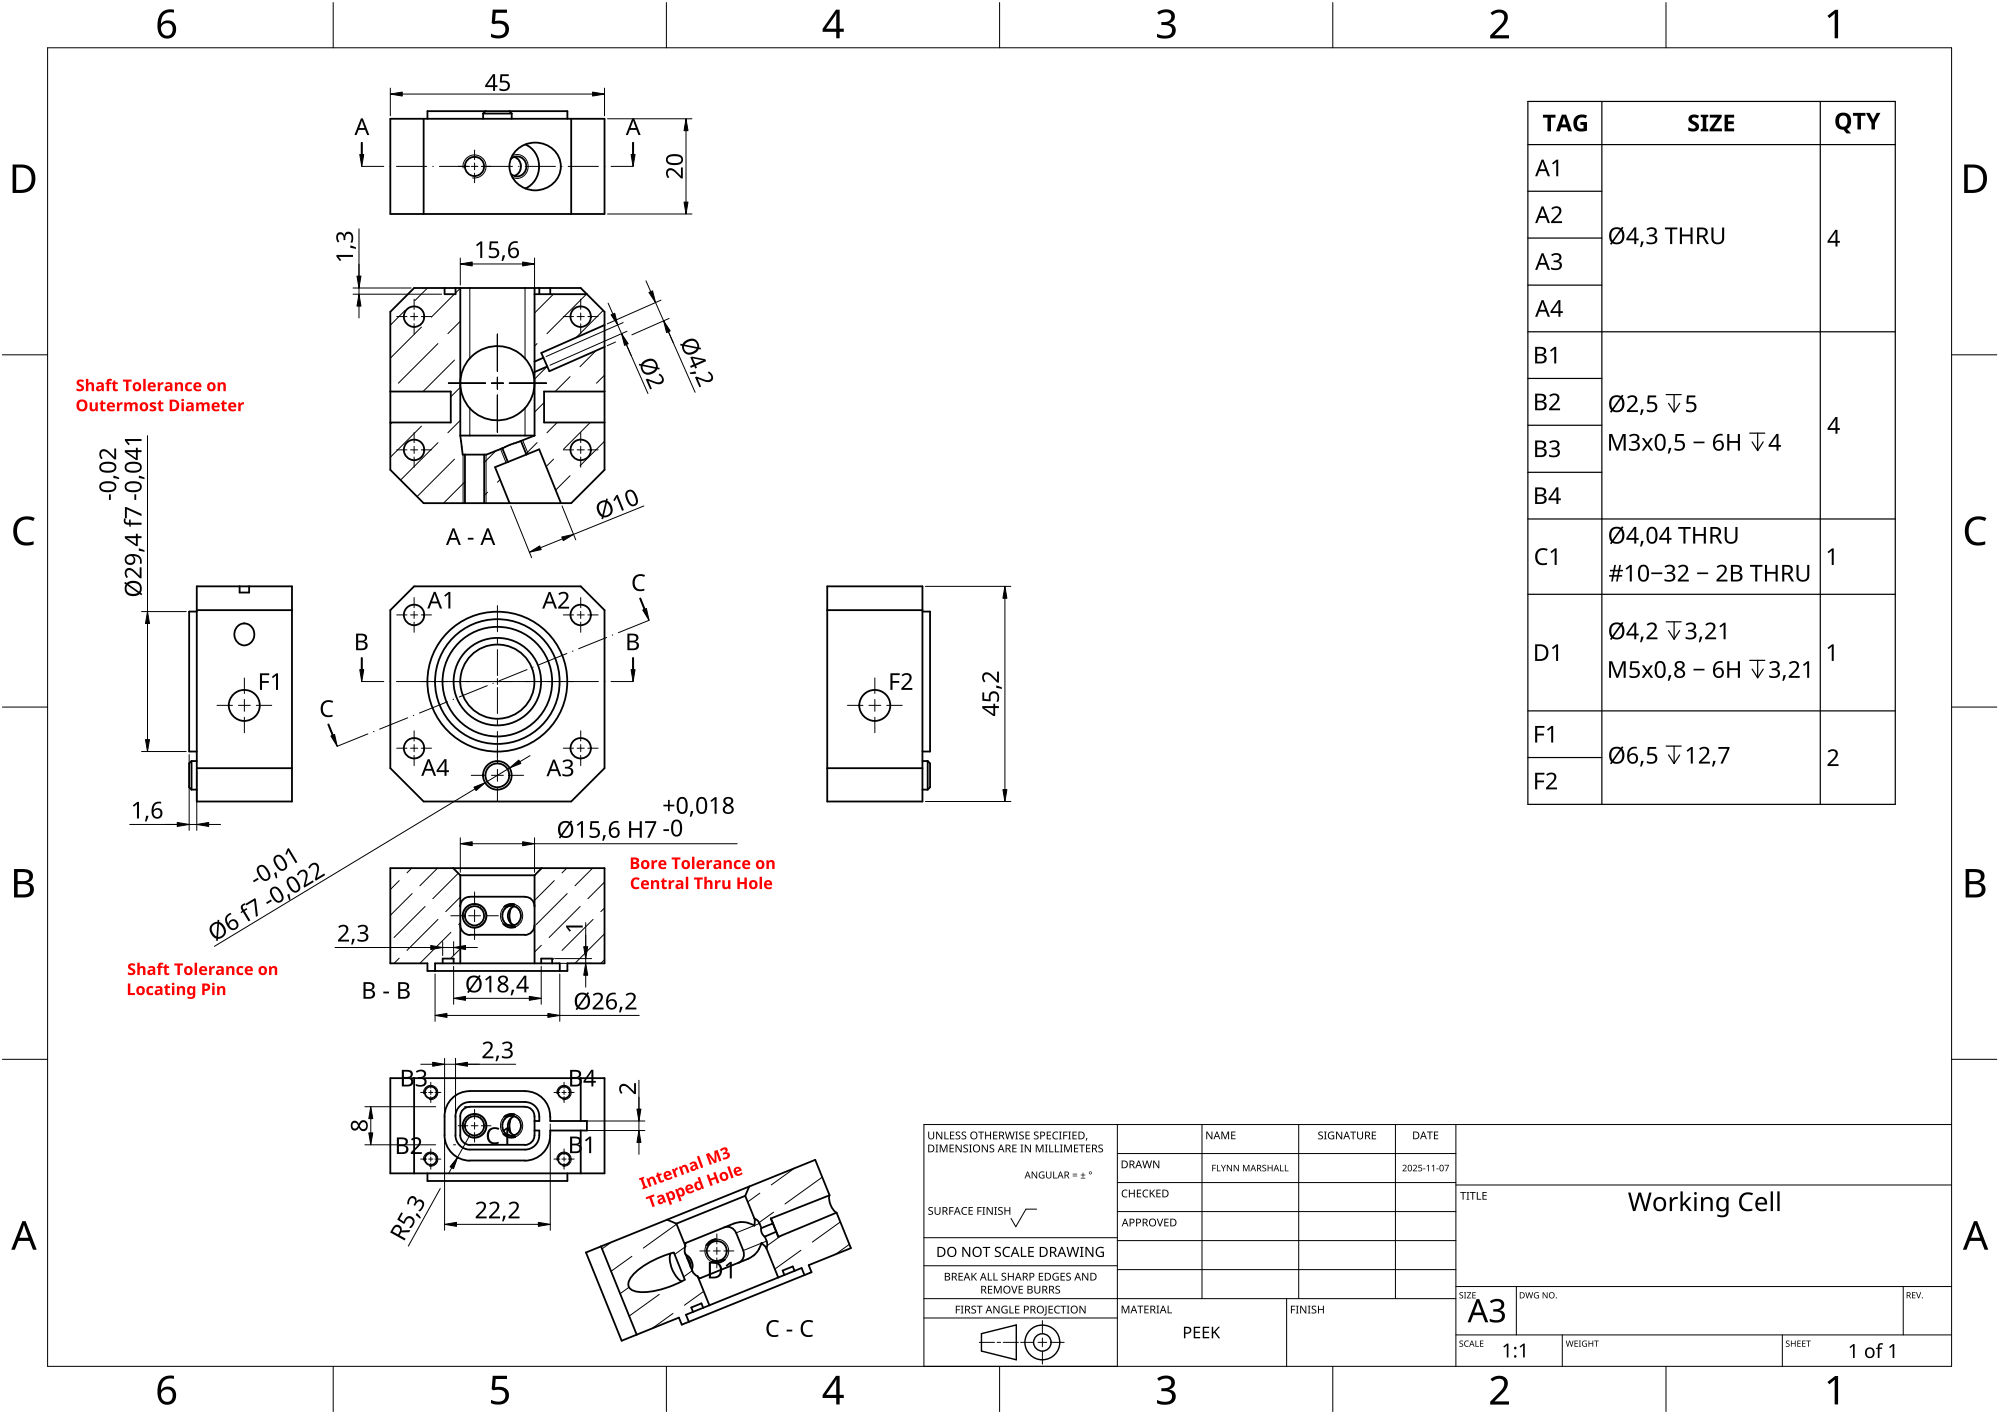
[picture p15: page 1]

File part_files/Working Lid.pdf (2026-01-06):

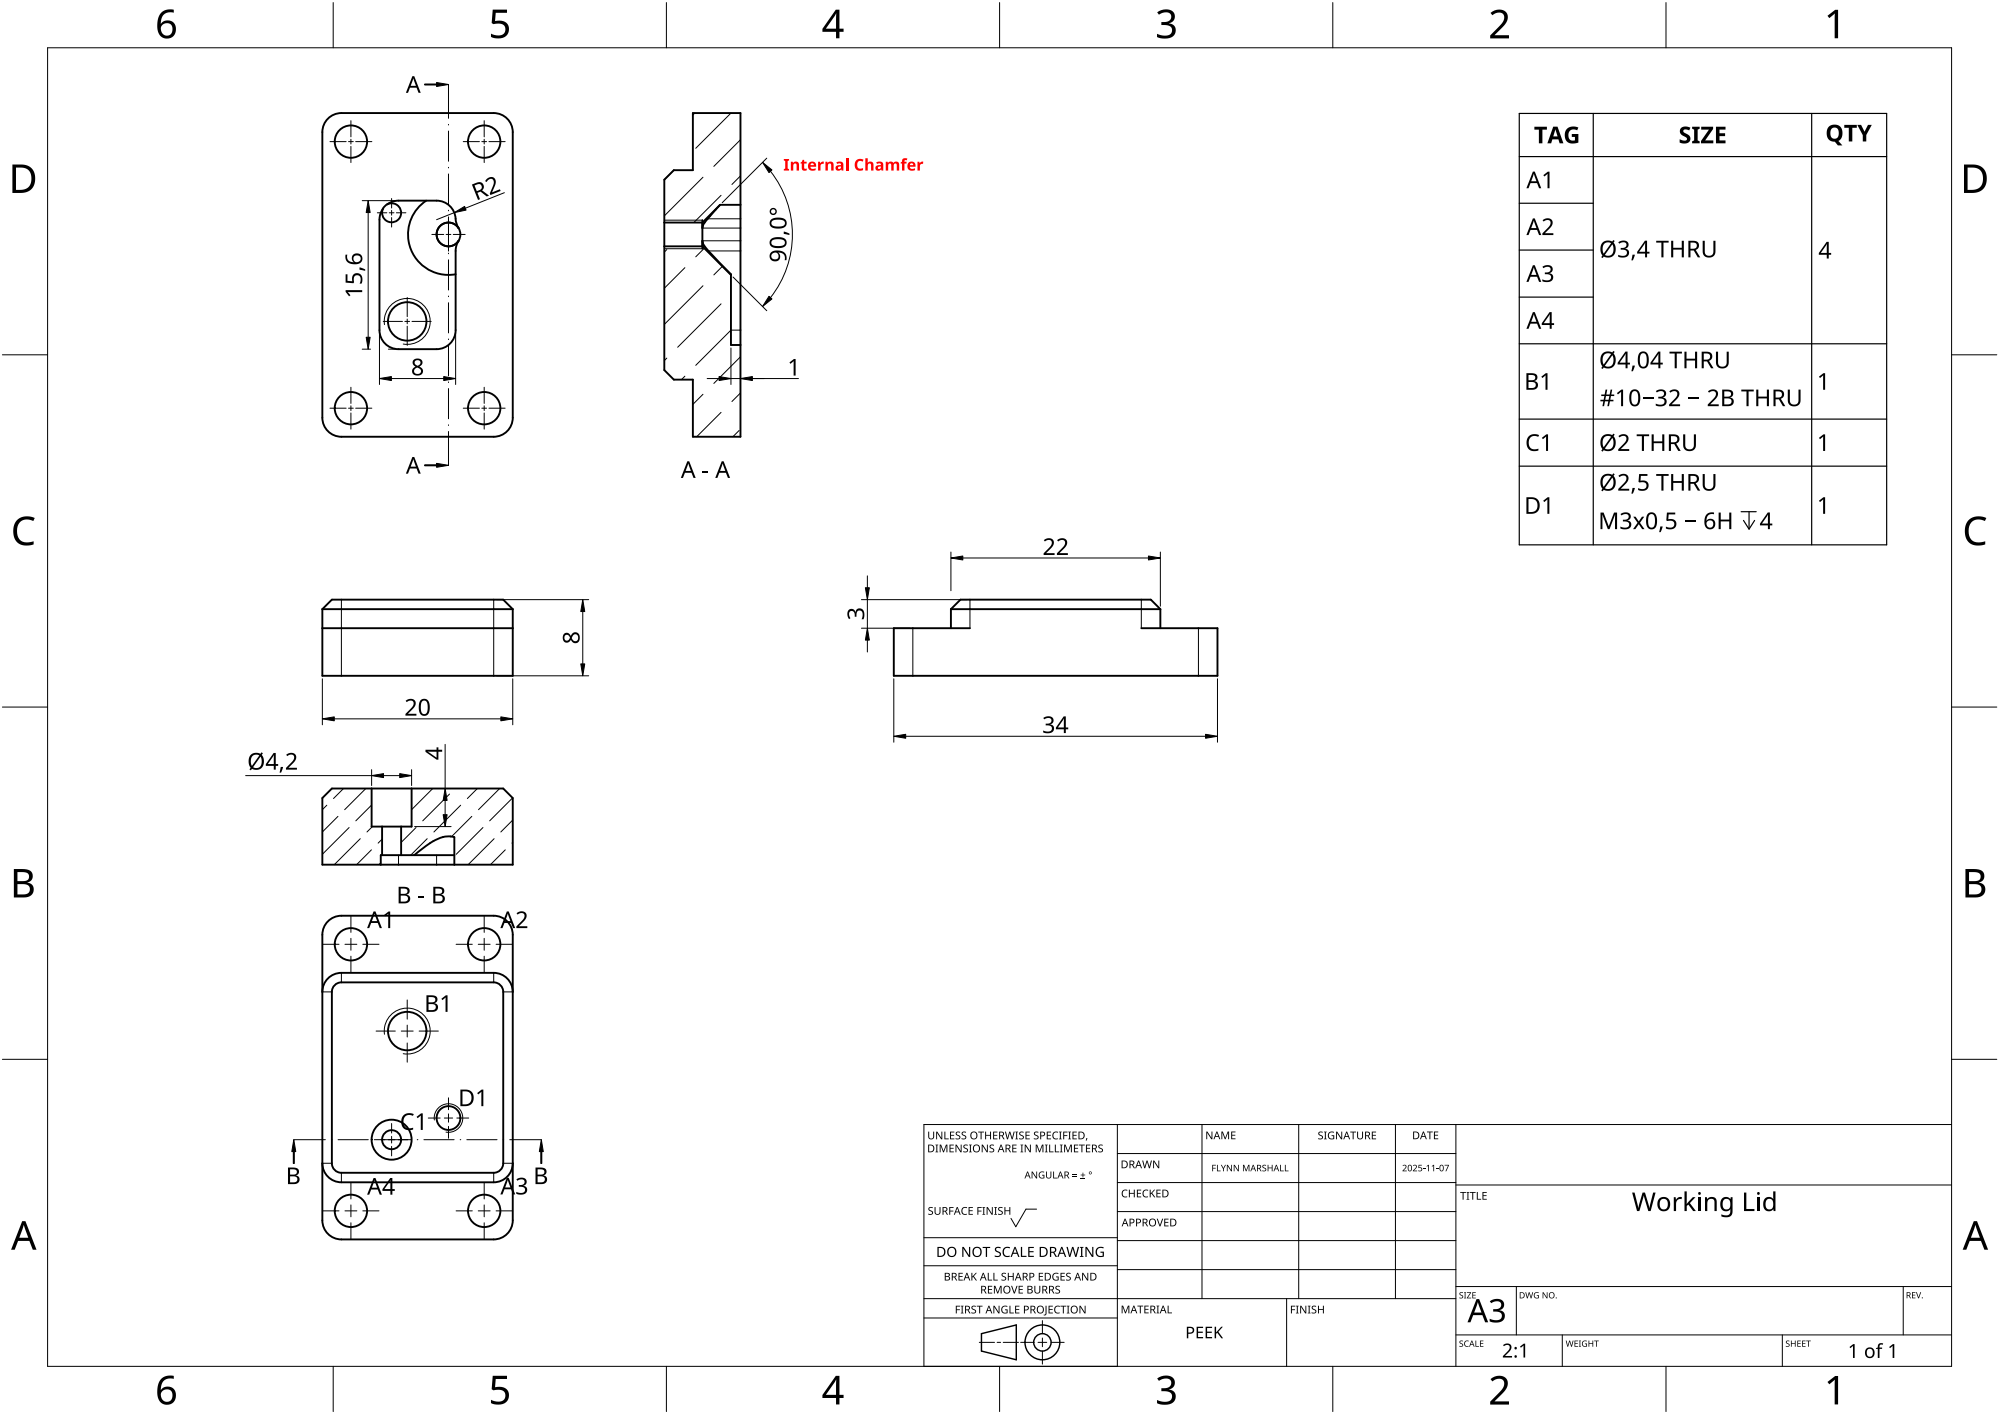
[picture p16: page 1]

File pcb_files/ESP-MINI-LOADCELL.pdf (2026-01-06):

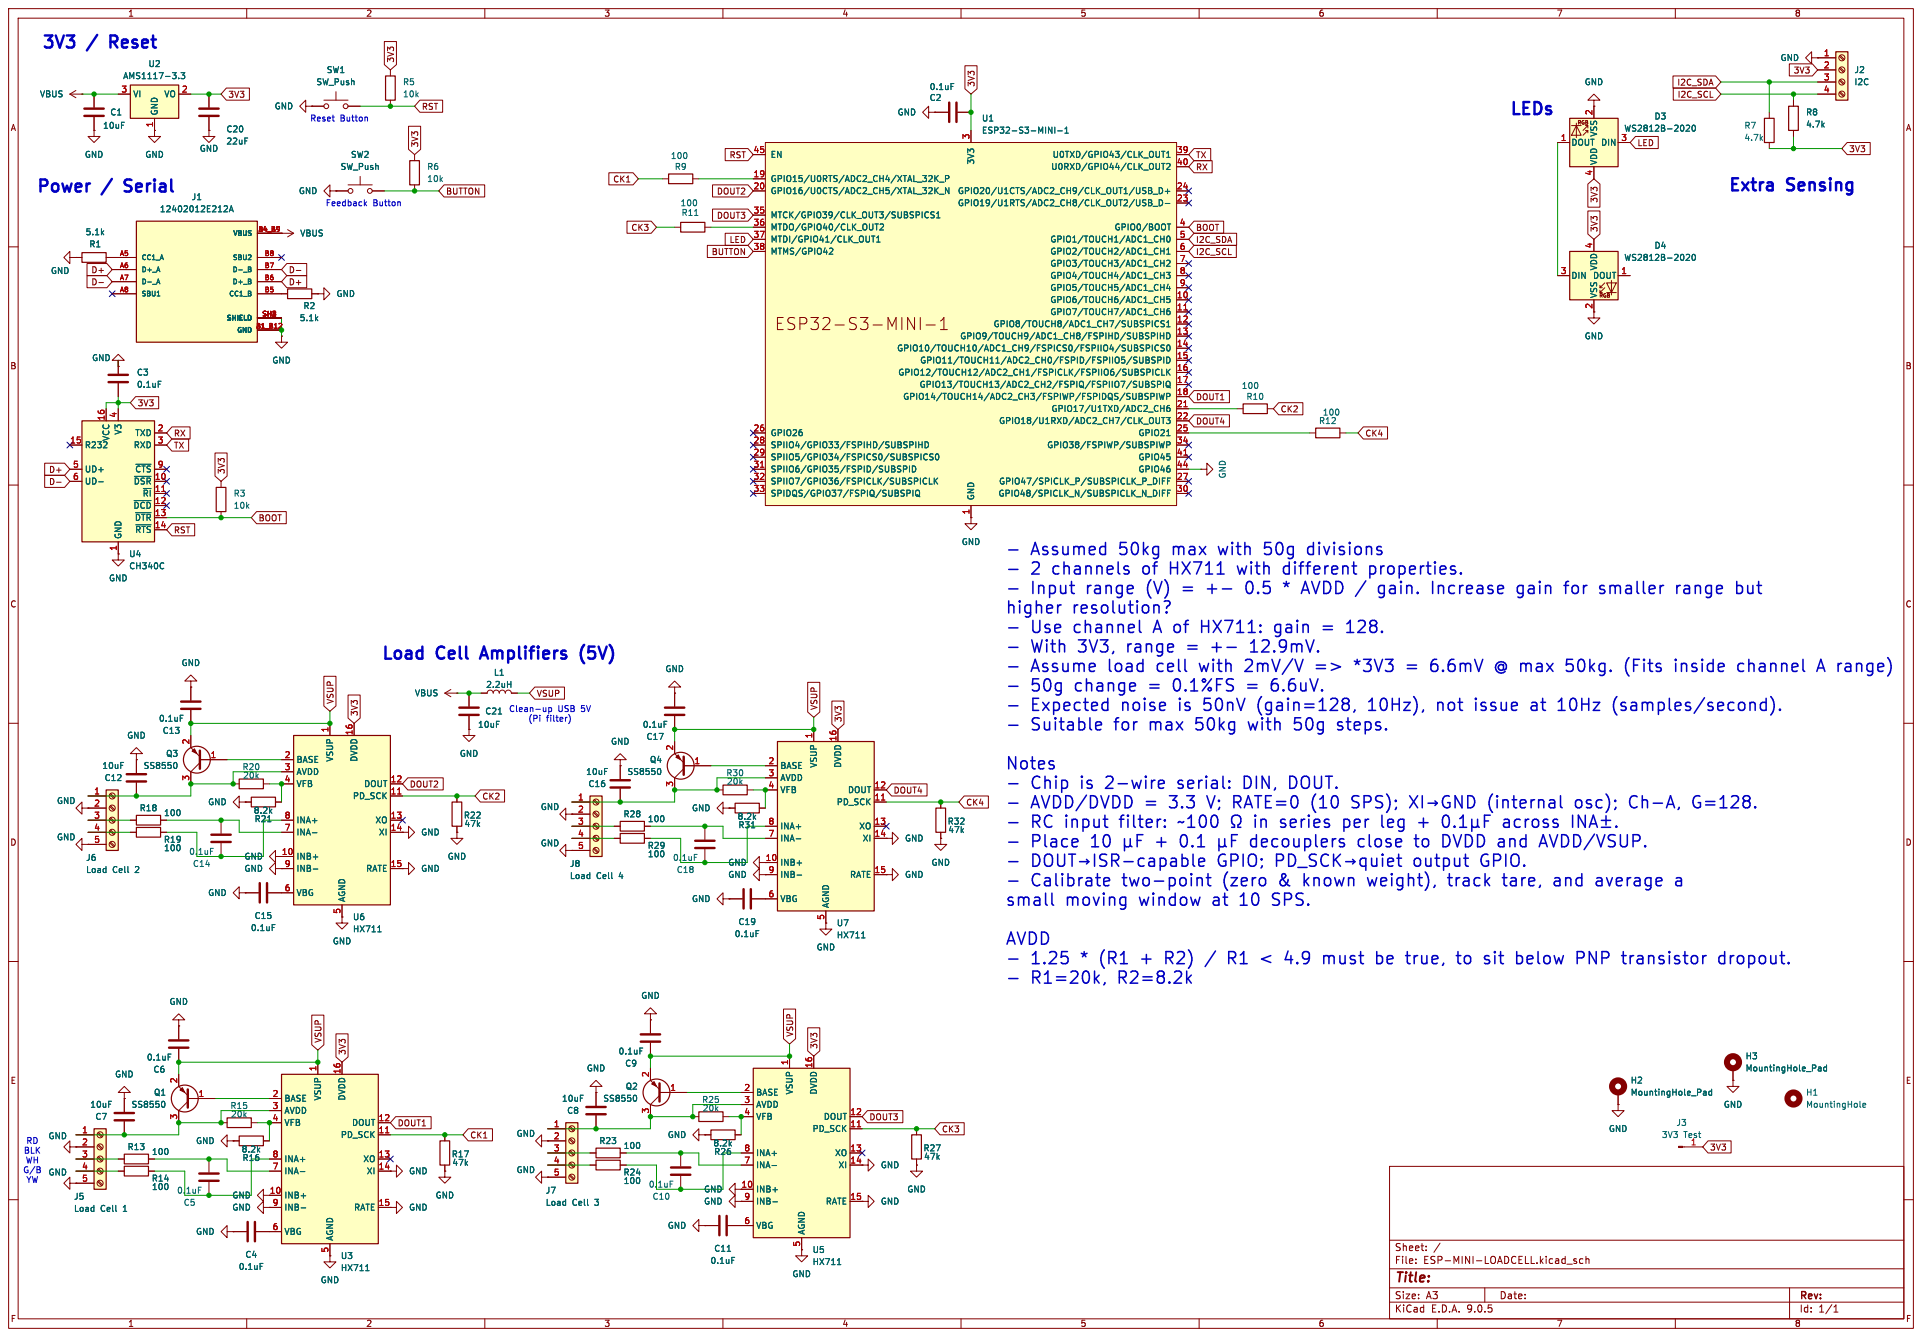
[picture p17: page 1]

1 VO 2 U2 AMS1117-3.3 R232 15 UD+ 5 UD- 6 VCC 16 V3

1 U0TXD/GPIO43/CLK_OUT1 39 U0RXD/GPIO44/CLK_OUT2 40 GPIO20/U1CTS/ADC2_CH9/CLK_OUT1/USB_D+ 24 GPIO19/U1RTS/ADC2_CH8/CLK_OUT2/USB_D- 23 GPIO0/BOOT 4 GPIO1/TOUCH1/ADC1_CH0 5 GPIO2/TOUCH2/ADC1_CH1 6 GPIO3/TOUCH3/ADC1_CH2 7 GPIO4/TOUCH4/ADC1_CH3 8 GPIO5/TOUCH5/ADC1_CH4 9 GPIO6/TOUCH6/ADC1_CH5 10 GPIO7/TOUCH7/ADC1_CH6 11 GPIO8/TOUCH8/ADC1_CH7/SUBSPICS1 12 GPIO9/TOUCH9/ADC1_CH8/FSPIHD/SUBSPIHD 13 GPIO10/TOUCH10/ADC1_CH9/FSPICS0/FSPIIO4/SUBSPICS0 14 GPIO11/TOUCH11/ADC2_CH0/FSPID/FSPIIO5/SUBSPID 15 GPIO12/TOUCH12/ADC2_CH1/FSPICLK/FSPIIO6/SUBSPICLK 16 GPIO13/TOUCH13/ADC2_CH2/FSPIQ/FSPIIO7/SUBSPIQ 17 GPIO14/TOUCH14/ADC2_CH3/FSPIWP/FSPIDQS/SUBSPIWP 18 GPIO17/U1TXD/ADC2_CH6 21 GPIO18/U1RXD/ADC2_CH7/CLK_OUT3 22 GPIO21 25 GPIO38/FSPIWP/SUBSPIWP 34 GPIO45 41 GPIO46 44 GPIO47/SPICLK_P/SUBSPICLK_P_DIFF 27 GPIO48/SPICLK_N/SUBSPICLK_N_DIFF 30 C2
GND

1 U0TXD/GPIO43/CLK_OUT1 39 U0RXD/GPIO44/CLK_OUT2 40 GPIO20/U1CTS/ADC2_CH9/CLK_OUT1/USB_D+ 24 GPIO19/U1RTS/ADC2_CH8/CLK_OUT2/USB_D- 23 GPIO0/BOOT 4 GPIO1/TOUCH1/ADC1_CH0 5 GPIO2/TOUCH2/ADC1_CH1 6 GPIO3/TOUCH3/ADC1_CH2 7 GPIO4/TOUCH4/ADC1_CH3 8 GPIO5/TOUCH5/ADC1_CH4 9 GPIO6/TOUCH6/ADC1_CH5 10 GPIO7/TOUCH7/ADC1_CH6 11 GPIO8/TOUCH8/ADC1_CH7/SUBSPICS1 12 GPIO9/TOUCH9/ADC1_CH8/FSPIHD/SUBSPIHD 13 GPIO10/TOUCH10/ADC1_CH9/FSPICS0/FSPIIO4/SUBSPICS0 14 GPIO11/TOUCH11/ADC2_CH0/FSPID/FSPIIO5/SUBSPID 15 GPIO12/TOUCH12/ADC2_CH1/FSPICLK/FSPIIO6/SUBSPICLK 16 GPIO13/TOUCH13/ADC2_CH2/FSPIQ/FSPIIO7/SUBSPIQ 17 GPIO14/TOUCH14/ADC2_CH3/FSPIWP/FSPIDQS/SUBSPIWP 18 GPIO17/U1TXD/ADC2_CH6 21 GPIO18/U1RXD/ADC2_CH7/CLK_OUT3 22 GPIO21 25 GPIO38/FSPIWP/SUBSPIWP 34 GPIO45 41 GPIO46 44 GPIO47/SPICLK_P/SUBSPICLK_P_DIFF 27 GPIO48/SPICLK_N/SUBSPICLK_N_DIFF 30 U1ESP32-S3-MINI-1 GND

1 TXD 2 RXD 3 ~{CTS}9 ~{DSR} 10 ~{RI} 11 ~{DCD} 12 ~{DTR} 13 ~{RTS} 14 U4 CH340C

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

- Assumed 50kg max with 50g divisions

5 DVDD 16 DOUT 12 PD_SCK 11 XO 13 XI 14 RATE 15 U6 HX711 GND GND GND GND GND
0.1uFGND GND

5 DVDD 16 DOUT 12 PD_SCK 11 XO 13 XI 14 RATE 15 GND GND GND GND

5 DVDD 16 DOUT 12 PD_SCK 11 XO 13 XI 14 RATE 15 U7 HX711 R32

5 DVDD 16 DOUT 12 PD_SCK 11 XO 13 XI 14 RATE 15 GND GND GND
47k GND GND GND

5 GND GND GND GND

small moving window at 10 SPS.

5 DVDD 16 DOUT 12 PD_SCK 11 XO 13 XI 14 RATE 15 C4
U3 HX711 BASE 2 AVDD 3 VFB 4

5 DVDD 16 DOUT 12 PD_SCK 11 XO 13 XI 14 RATE 15 U5 HX711 C11
BASE 2 AVDD 3 VFB 4

5 DVDD 16 DOUT 12 PD_SCK 11 XO 13 XI 14 RATE 15 C11
U5 HX711 BASE 2 AVDD 3 VFB 4

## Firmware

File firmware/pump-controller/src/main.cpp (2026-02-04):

#include <Arduino.h>
#include <esp_sleep.h>
#include <Adafruit_NeoPixel.h>
#include <Adafruit_SHT4x.h>
#include <ArduinoOTA.h>
#include <WiFi.h>

#include <AccelStepper.h>
#include <Adafruit_GFX.h>
#include <Adafruit_SSD1306.h>

// Local modules
#include "led_animations.h"

// ---------------- Pinout ----------------
#define ADC1 GPIO_NUM_1
#define ADC2 GPIO_NUM_2
#define ADC3 GPIO_NUM_4

#define SDA GPIO_NUM_42
#define SCL GPIO_NUM_41

#define PWM1 GPIO_NUM_40
#define DIR1 GPIO_NUM_39

#define PWM2 GPIO_NUM_38
#define DIR2 GPIO_NUM_37

#define PWM3 GPIO_NUM_36
#define DIR3 GPIO_NUM_35

#define PWM4 GPIO_NUM_48
#define DIR4 GPIO_NUM_47

#define STEP5 GPIO_NUM_16
#define DIR5  GPIO_NUM_8
#define EN5   GPIO_NUM_15

#define STEP6 GPIO_NUM_6
#define DIR6  GPIO_NUM_7
#define EN6   GPIO_NUM_5

#define STEP7 GPIO_NUM_14
#define DIR7  GPIO_NUM_13
#define EN7   GPIO_NUM_21

#define STEP8 GPIO_NUM_11
#define DIR8  GPIO_NUM_10
#define EN8   GPIO_NUM_12

#define LEDPIN  GPIO_NUM_9
#define SERVO1  GPIO_NUM_18
#define SERVO2  GPIO_NUM_17

#define BUTTON  GPIO_NUM_0

// ---------------- Display ----------------
#define SCREEN_WIDTH 128
#define SCREEN_HEIGHT 64
#define OLED_RESET -1
Adafruit_SSD1306 display(SCREEN_WIDTH, SCREEN_HEIGHT, &Wire, OLED_RESET);

// ---------------- Steppers ----------------
AccelStepper STEPPER1(AccelStepper::DRIVER, STEP5, DIR5); 
AccelStepper STEPPER2(AccelStepper::DRIVER, STEP6, DIR6);
AccelStepper STEPPER3(AccelStepper::DRIVER, STEP7, DIR7);
AccelStepper STEPPER4(AccelStepper::DRIVER, STEP8, DIR8);

AccelStepper* steppers[4] = {&STEPPER1, &STEPPER2, &STEPPER3, &STEPPER4};
const int pwm_pins[4] = {PWM1, PWM2, PWM3, PWM4};
const int dir_pins[4] = {DIR1, DIR2, DIR3, DIR4};
const int en_pins[4]  = {EN5, EN6, EN7, EN8};

// ---------------- Sensors ----------------
#define SHT4x_DEFAULT_ADDR 0x46
Adafruit_SHT4x sht4 = Adafruit_SHT4x();
sensors_event_t hum, temp;

// ---------------- LED Animations ----------------
#define NUMPIXELS 7
static const uint8_t OUTER[6] = {0,1,2,3,4,5};
static const uint8_t CENTER_IDX = 6;
LedAnimations LEDS;

// ---------------- Kinematics ----------------
const float STEPS_REV   = 200.0;
const float MICROSTEPS  = 4.0;
const float ML_REV      = 0.094;   // ml/rev
const float back_flow   = 0.02;    // ml
const float default_flow_rate = 0.05; // ml/s
const float MAX_ACCEL   = 500.0 * MICROSTEPS; // microsteps/s^2

// ---------------- Globals used in loop/handlers ----------------
float measured_temp = 0.0;
float measured_hum  = 0.0;

float flow_rate;
float vol;
float volumes[4];
float pwm;
float seconds;
int   motor;

String action;
String buffer;

unsigned long CurrentTime;
unsigned long ElapsedTime;
unsigned long LastCall = 0;
const unsigned long screenReset = 120;

// ------ Prototypes ------
void pwmDrivingSignal(int motor, int power);
long volToSteps(float vol);
void runSteppers();
void driveStepper(int motor, float vol, float flow_rate = default_flow_rate, float back_flow = back_flow);
void driveAllSteppers(float volumes[4], float flow_rate = default_flow_rate, float back_flow = back_flow);
int16_t printWrappedChars(Adafruit_SSD1306& d, const String& text, int16_t x, int16_t y, uint8_t maxCharsPerLine, uint8_t lineHeightPx);
void updateEnvironmentReadings();

// ---------------- Setup ----------------
void setup() {
  Serial.begin(115200);

  // GPIO + PWM + steppers
  for (int i = 0; i < 4; i++) {
    pinMode(pwm_pins[i], OUTPUT);
    pinMode(dir_pins[i], OUTPUT);
    pinMode(en_pins[i], OUTPUT);

    digitalWrite(pwm_pins[i], LOW);
    digitalWrite(dir_pins[i], LOW);
    digitalWrite(en_pins[i], HIGH);

    ledcSetup(i, 10000, 10);
    ledcAttachPin(pwm_pins[i], i);

    steppers[i]->setAcceleration(MAX_ACCEL);
    steppers[i]->setMaxSpeed((float)volToSteps(default_flow_rate));
  }

  // I2C + sensors + display
  Wire.begin(SDA, SCL, 400000);
  sht4.begin(&Wire);
  sht4.setPrecision(SHT4X_HIGH_PRECISION);

  display.begin(SSD1306_SWITCHCAPVCC, 0x3C);

  // LEDs
  pinMode(LEDPIN, OUTPUT);
  LEDS.begin(LEDPIN, NUMPIXELS, CENTER_IDX, OUTER, 6, BLUE);

  pinMode(BUTTON, INPUT);

  Serial.println("Available functions:");
  Serial.println("singleStepperPump(int motor, float volume [ml], float flow_rate [ml/s])");
  Serial.println("multiStepperPump(float v1 [ml], float v2 [ml], float v3 [ml], float v4 [ml], float flow_rate [ml/s])");
  Serial.println("setPWM(int motor, float power [+-%])");
  Serial.println("getTemperature()");
  Serial.println("getHumidity()");
  Serial.println("statusCheck()");

  Serial.println("# Controller available");
  LEDS.spinnerTimer(1, GREEN);
}

// ---------------- Loop ----------------
void loop() {
  delay(1000);

  // Read either BLE message or Serial command
  if (Serial.available() > 0) {
    LEDS.pulse(PURPLE);

    action = Serial.readStringUntil('(');

    if (action == "singleStepperPump") {
      motor     = Serial.readStringUntil(',').toInt();
      vol       = Serial.readStringUntil(',').toFloat();
      flow_rate = Serial.readStringUntil(')').toFloat();

      driveStepper(motor, vol, flow_rate);
      Serial.println("# Pump action complete");
    }
    else if (action == "multiStepperPump") {
      volumes[0] = Serial.readStringUntil(',').toFloat();
      volumes[1] = Serial.readStringUntil(',').toFloat();
      volumes[2] = Serial.readStringUntil(',').toFloat();
      volumes[3] = Serial.readStringUntil(',').toFloat();
      flow_rate  = Serial.readStringUntil(')').toFloat();

      driveAllSteppers(volumes, flow_rate);
      Serial.println("# Pump action complete");
    }
    else if (action == "setPWM") {
      motor   = Serial.readStringUntil(',').toInt();
      pwm     = Serial.readStringUntil(')').toFloat();
      pwmDrivingSignal(motor, pwm);
      Serial.println("# PWM set");
    }
    else if (action == "getTemperature") {
      (void)Serial.readStringUntil(')');
      updateEnvironmentReadings();
      Serial.println(String(measured_temp, 2));
    }
    else if (action == "getHumidity") {
      (void)Serial.readStringUntil(')');
      updateEnvironmentReadings();
      Serial.println(String(measured_hum, 2));
    }
    else if (action == "statusCheck") {
      (void)Serial.readStringUntil(')');
      Serial.println("# Controller available");
    }
    else {
      Serial.println("Unknown command: " + action);
      LEDS.pulse(RED, 3);
    }

  }
  else {
    CurrentTime = ceil(millis() / 1000.0);
    ElapsedTime = CurrentTime - LastCall;

    if (ElapsedTime > screenReset) {
      LastCall = CurrentTime;
    }

  }
}

// ---------------- Implementation ----------------

long volToSteps(float vol) {
  return floor(MICROSTEPS * STEPS_REV * vol / ML_REV);
}

void runSteppers() {
  // Enable all drivers
  for (int i = 0; i < 4; i++) digitalWrite(en_pins[i], LOW);

  bool anyRunning;
  do {
    LEDS.run(); // non-blocking spinner
    anyRunning = false;
    for (int i = 0; i < 4; i++) {
      if (steppers[i]->distanceToGo() != 0) {
        steppers[i]->run();
        anyRunning = true;
      } else {
        digitalWrite(en_pins[i], HIGH); // disable when done
      }
    }
  } while (anyRunning);
}

void driveStepper(int motor, float vol, float flow_rate, float back_flow_local) {
  if (motor < 1 || motor > 4) {
    Serial.println("Error: Invalid stepper index (must be 1-4)");
    return;
  }

  digitalWrite(en_pins[motor - 1], LOW);
  steppers[motor - 1]->setMaxSpeed((float)volToSteps(flow_rate));

  steppers[motor - 1]->move(volToSteps(vol + back_flow_local));
  runSteppers();

  steppers[motor - 1]->move(volToSteps(-1 * back_flow_local));
  runSteppers();

  digitalWrite(en_pins[motor - 1], HIGH);

  LEDS.pulse(ORANGE);
}

void driveAllSteppers(float volumes[4], float flow_rate, float back_flow_local) {
  for (int i = 0; i < 4; i++) {
    if (volumes[i] != 0) {
      steppers[i]->setMaxSpeed((float)volToSteps(flow_rate));
      steppers[i]->move(volToSteps(volumes[i] + back_flow_local));
    }
  }
  runSteppers();

  for (int i = 0; i < 4; i++) {
    if (volumes[i] != 0) {
      steppers[i]->move(volToSteps(-1 * back_flow_local));
    }
  }
  runSteppers();

  LEDS.pulse(ORANGE);
}

void pwmDrivingSignal(int motor, int power) {
  power = constrain(power, -100, 100);

  if (motor < 1 || motor > 4) {
    Serial.println("Error: Invalid motor index. Must be 1–4.");
    return;
  }

  int dir_pin = dir_pins[motor - 1];
  if (power >= 0) {
    digitalWrite(dir_pin, HIGH);  // Forward
    ledcWrite(motor - 1, 1023 - map(power, 0, 100, 0, 1023));
  } else {
    digitalWrite(dir_pin, LOW);   // Reverse
    ledcWrite(motor - 1, map(-power, 0, 100, 0, 1023));
  }
}

void updateEnvironmentReadings() {
  sht4.getEvent(&hum, &temp);
  measured_temp = temp.temperature;
  measured_hum  = hum.relative_humidity;
}

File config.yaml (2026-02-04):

serial:
  load_cell_board:
    port: /dev/cu.wchusbserial1220
    baud: 115200
  mfc_stepper_valve_board:
    port: /dev/cu.wchusbserial1230
    baud: 115200
  pump_board:
    port: /dev/cu.wchusbserial110
    baud: 115200
    
system:
  cells:
  - 1
  - 2
  - 3
  - 4
  valves:
    '1': 1
    '2': 2
    '3': 3
    '4': 4

topup:
  density_g_per_ml: 1.0
  target_volume_ml: 150.0
  min_volume_ml: 120.0
  pump_pwm: 0.65
  pump_rate_ml_per_s: 0.9
  max_pump_s_per_cell: 30.0
  recheck_after_pump_s: 2.0
  max_attempts: 3

defaults:
  electrolyte_stepper_flow_rate_ml_per_s: 0.08

experiment:
  name: example_parallel_4cell_run
  steps:

  - name: prime_flows
    type: flow
    duration_s: 300
    co2_flow_sccm: 50.0
    electrolyte_flow_rate_ml_per_s: 0.08
    divert_cell: null

  - name: topup_before_measurement
    type: topup

  - name: measurement_placeholder
    type: measure
    duration_s: 600
    note: Placeholder for Biologic VSP-300 control (one channel per cell).

  - name: divert_cell_2_to_analyzer
    type: divert
    cell: 2
    duration_s: 120

  - name: stop_co2
    type: co2_off

  - name: deprime_reverse_liquid
    type: deprime
    duration_s: 180
    electrolyte_flow_rate_ml_per_s: 0.06

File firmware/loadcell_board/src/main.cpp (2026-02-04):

#include <Arduino.h>
#include "leds.h"
#include "loadcells.h"

#include <string>
#include <stdio.h>

// --- Pins ---
static const uint8_t PIN_BUTTON_TARE = 42;   // active LOW with internal pull-up

// --- State ---
static const uint16_t BTN_DEBOUNCE_MS = 30;
static const uint16_t BTN_TARE_TRIGGER_MS = 60;

// --- add near top of main.cpp, after other consts ---
static float CAL_KNOWN_LOAD_KG  = 200.0f;       // EDIT to your calibration mass
static const uint32_t BTN_LONG_MS       = 5000;      // 5 seconds to enter calibration
static bool     btnDown = false;
static uint32_t btnDownAt = 0;

float masses[NUM_CHANNELS] = {0};
float mass = 0;
String action;
#define MSG_BUF_SIZE 256

// --- LED config (moved implementation to led.*) ---
#define NUMPIXELS 2
#define LEDPIN 41
static const uint8_t OUTER[2] = {0,1};
static const uint8_t CENTER_IDX = 0; //not used
LedAnimations LEDS;

void setup() {
  Serial.begin(115200);
  delay(200);

  Serial.println("Load Cell Board V1");
  Serial.println("Preparing load cells..");

  // Load cells first (takes a while)
  loadcellsInit(); 

  // LED init
  pinMode(LEDPIN, OUTPUT);
  LEDS.begin(LEDPIN, NUMPIXELS, CENTER_IDX, OUTER, 6);

  // Button
  pinMode(PIN_BUTTON_TARE, INPUT_PULLUP);               

  Serial.println("Available functions:");
  Serial.println("readCell(int cell)");
  Serial.println("tareCell(int cell)");
  Serial.println("tareAll()");
  Serial.println("calibrateCell(int cell)");
  Serial.println("statusCheck()");
  Serial.println("changeCalWeight(float weight)");

  Serial.println("# Controller available");
  LEDS.pulse(HAPPY);
}

void loop() {
  delay(200);

  // Read either BLE message or Serial command
  if (Serial.available() > 0) {
    LEDS.pulse(TRANSMIT);

    action = Serial.readStringUntil('(');

    if (action == "readCell") {
      int cell = Serial.readStringUntil(')').toInt();

      bool ok = loadcellRead(cell, mass);
      if (!ok) {
        LEDS.pulse(ERROR, 2);
        Serial.println("Failed to read load cell");
      }
      else {
        Serial.println(String(mass, 3));
      }
    }

    else if (action == "tareCell") {
      int cell = Serial.readStringUntil(')').toInt();

      loadcellTare(cell);
      LEDS.pulse(HAPPY, 1, 20);

      Serial.println("# Done");
    }

    else if (action == "calibrateCell") {
      int cell = Serial.readStringUntil(')').toInt();
      
      bool ok = loadcellCalibrate(cell, CAL_KNOWN_LOAD_KG);
      if (!ok) {
        LEDS.pulse(ERROR, 2);
        Serial.println("Failed to calibrate load cell");
      }
      else {
        LEDS.pulse(HAPPY, 1, 20);
        Serial.println("# Done");
      }
    }

    else if (action == "tareAll") {
      (void)Serial.readStringUntil(')');
      loadcellsTareAll();
      Serial.println("# Done");
    }

    else if (action == "statusCheck") {
      (void)Serial.readStringUntil(')');
      Serial.println("# Ready");
      LEDS.pulse(BLUETOOTH);
    }

    else if (action == "changeCalWeight") {
      CAL_KNOWN_LOAD_KG = Serial.readStringUntil(')').toFloat();
      Serial.println("# Done");
    }

    else {
      (void)Serial.readStringUntil(')');
      Serial.println("Unknown command: " + action);
      LEDS.pulse(ERROR, 2);
    }
  }
}

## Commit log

2026-01-06 Push all part files and firmware
    [ANODE_PLATE_TI - REV1.step, CATHODE_PLATE_TI - REV1.step, H-Cell - Counter Cell.step, H-Cell - Counter Lid.step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]
2026-01-19 Simplified load cell calibration
